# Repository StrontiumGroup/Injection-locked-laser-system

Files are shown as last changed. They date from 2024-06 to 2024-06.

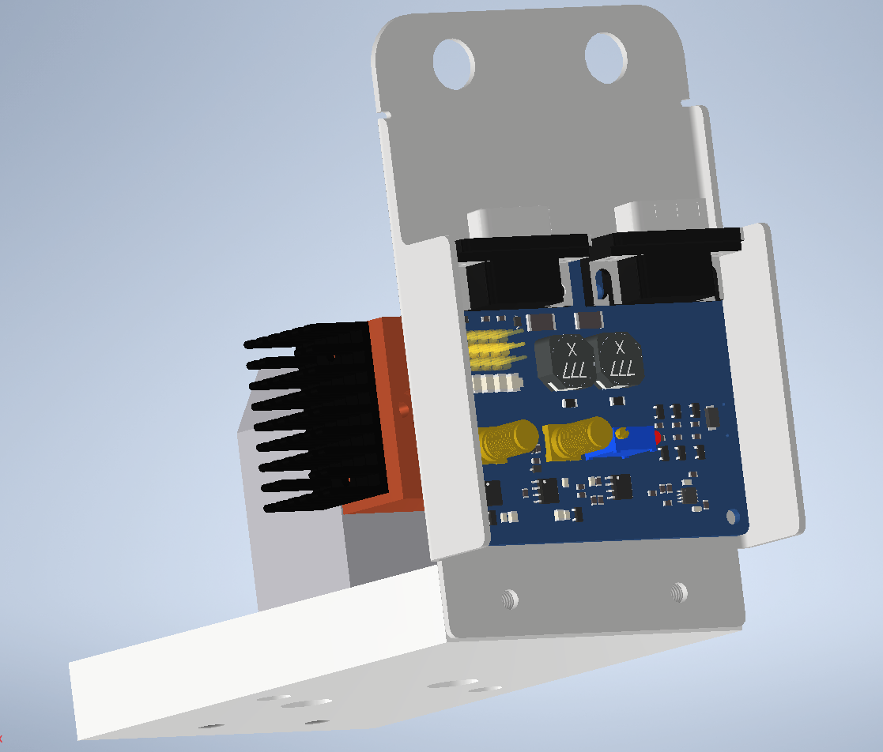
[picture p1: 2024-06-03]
Pictures/Assembly1.png

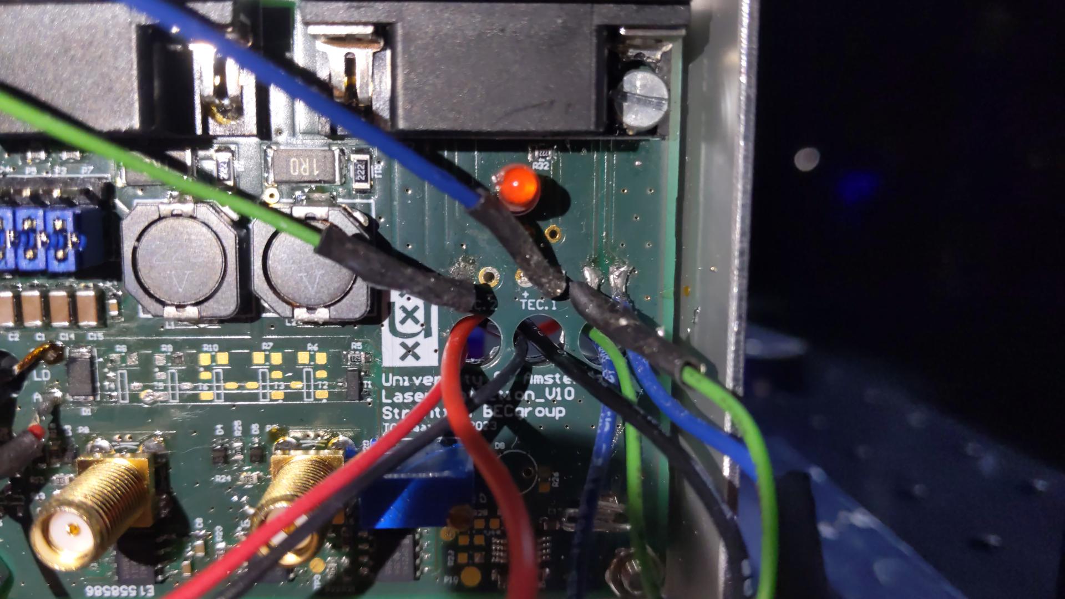
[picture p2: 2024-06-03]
Pictures/SN1/sn1_b.jpeg

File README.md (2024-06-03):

23-0064 Laser diode collimator holder-01
WhatsApp Image 2024-06-03 at 14 32 54 (1)
WhatsApp Image 2024-06-03 at 14 32 54
Assembly1
Assingment


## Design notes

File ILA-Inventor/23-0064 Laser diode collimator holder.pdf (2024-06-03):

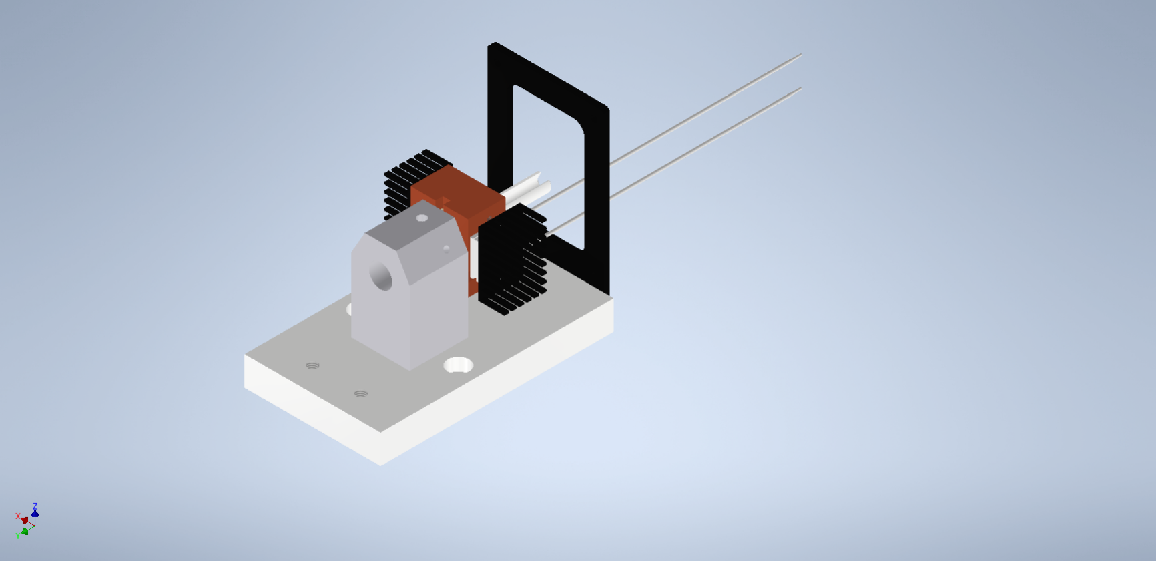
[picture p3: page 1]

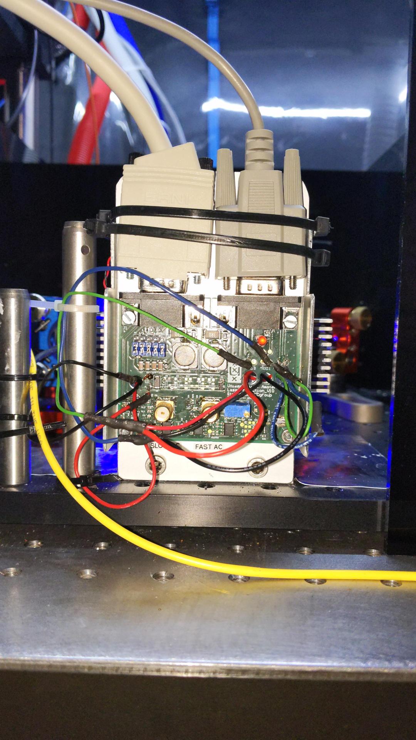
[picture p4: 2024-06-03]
Pictures/SN1/sn1_a.jpeg

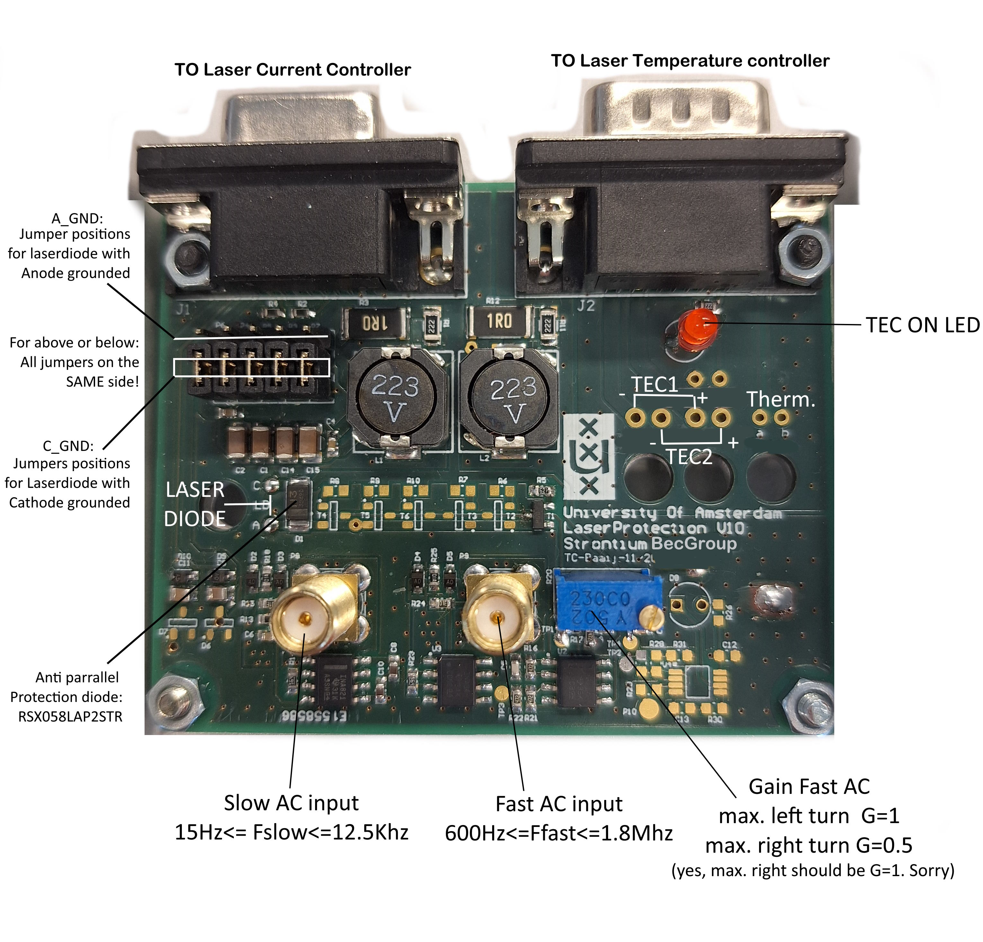
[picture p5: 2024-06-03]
Pictures/SN2/Assingment.jpg

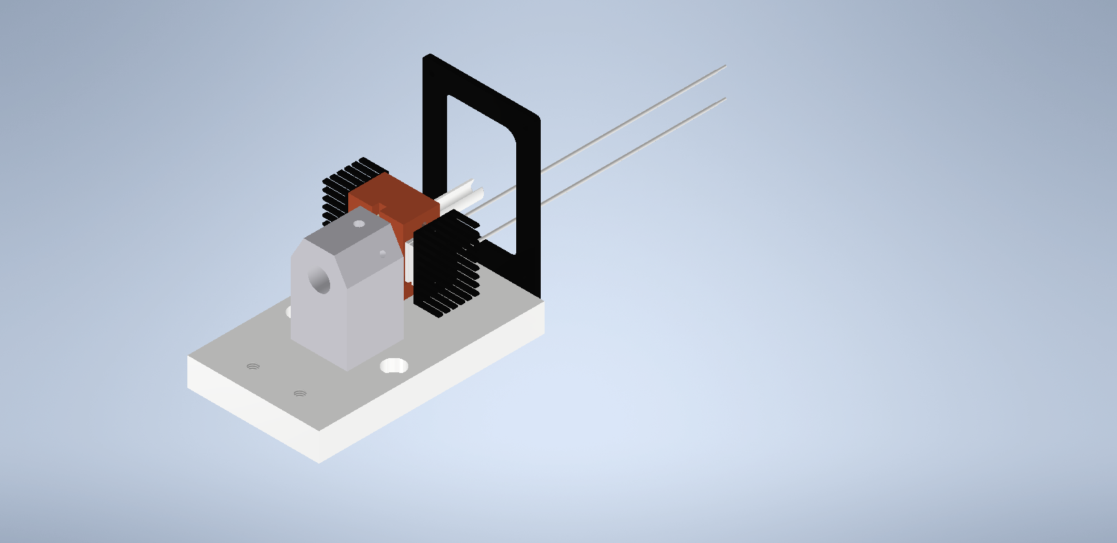
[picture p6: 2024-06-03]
ILA-Inventor/23-0064 Laser diode collimator holder.png

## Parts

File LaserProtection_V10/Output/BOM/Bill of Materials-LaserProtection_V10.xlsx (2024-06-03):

Designator | Quantity | Partname | Description | Footprint | Supplier 1 | Supplier Part Number 1
C1, C2, C14, C15 | 4 | C3216X5R1A107M160AC | MLCC 100 µF, 10 V, 1206 [3216 Metric], ± 20%, X5R | cap1206MD | Farnell | 2211193
C3, C4 | 2 | Cap0603MD_100n_X7R_50V_10% |  | cap0603MD | Farnell | 2581046
C5 | 1 | Cap0603MD_5p_NP0_50V_5% |  | cap0603MD | Farnell | 1759046
C6 | 1 | Cap0603MD_1n5_NP0_50V_5% |  | cap0603MD | Farnell
C7, C8, C10, C12 | 4 | Cap0603MD_1u_X5R_50V_10% |  | cap0603MD | Farnell | 3013383
C9, C11 | 2 | Cap0805MD_10u_X5R_25V_10% |  | cap0805MD | Farnell | 1735530
C13 | 1 | Cap0603MD_10u_X7R_10V_10% |  | cap0603MD | Mouser | 81-GRM188Z71A106KA3D
D1 | 1 | RSX058LAP2STR | Schottky Diode, 3A, 200V, Vf=0.84 (3A/35C), Ir=5-100nA | SODFL470X110-2N | Mouser | 755-RSX058LAP2STR
D2, D3, D4, D5, D9, D10 | 6 | PESD12VL1BA,115 | TVS Diode, Bidirectional, 12V, SOD-323, 2 Pins | SOD-323-2-NoPol | Farnell | 8737363
D6, D7 | 2 | PLVA665A,215 | Zener 6v5, 250mW, 3%, SOT-23 | SOT95P230X110-3N | Mouser | 771-PLVA665A215
D8, D11 | 2 | LED_3mm | Generic 3mm LED Footprint | LED_3mm | Mouser | 710-151031SS04000
Graph1 | 1 | UvA_Logo_Small_horizontal | University of Amsterdam Logo | UVA_LOGO_SMALL_HOR | <no part>
J1 | 1 | 182-009-213R531 | NorComp, D-SUB, 9 pins, Female, right angled PCB | 182-009-213Ryy1 | Farnell | 2294288
J2 | 1 | 182-009-113R531 | NorComp, D-SUB, 9 pins, Male, right angled PCB | 182-009-113Ryy1 | Farnell | 2294285
L1, L2 | 2 | MSS1048T-223MLC | Power Inductor, SMD, 22 µH, 3.58 A, Shielded, 2.36 A | INDP102100X51N | Farnell | 2288292
MH1, MH2 | 2 | MountingHole M3 NP | MountingHole NP for M3, drill 3.2mm, keepout dia 6.5 | MountHole M3 NP keepout 6_5mm | Farnell
MH3, MH4, MH5, MH6 | 4 | MountingHole 5.0mm No keepout | MountingHole 5mm No keepout | MountHole 5mm NP No keepout | Farnell
P1, P2 | 2 | SolderPad_PT_c1.5h0.7mm | SolderPad_PT_c1.5h0.7mm | Pad_PT_c15h07mm | Farnell
P3, P4, P5, P6, P7 | 5 | Header254-1x3 | Header 2.54p 1x3 | Header254-1x3 | Farnell | 1022248
P8, P9 | 2 | PCB.114SMAFSTJ.A | SMA Coaxial, 17.7mm, 50 Ohm, Straight Jack, Through Hole | PCB114SMAFSTJ | Mouser | 960-PCB.114SMAFSTJ.A
P10 | 1 | SolderPad_SMD_c2.0mm | SolderPad_SMD_c2.0mm | Pad_SMD_c20mm | Farnell
P11, P12, P13, P14 | 4 | SolderPad_PT_c1.6h0.8mm | SolderPad_PT_c1.6h0.8mm | Pad_PT_c16h08mm | Farnell
P15, P16, P17, P18 | 4 | SolderPad_PT_c2.0h1.0mm | SolderPad_PT_c2.0h1.0mm | Pad_PT_c20h10mm | Farnell
R1, R11 | 2 | Res1206MD_2K2_1% |  | res1206MD | Farnell
R2, R4, R13 | 3 | Res0603MD_10K_1% |  | res0603MD | Farnell | 2446547
R3, R12 | 2 | RC2512JK-7W4R7L | SMD Chip Resistor, 4.7 ohm, ± 5%, 2 W, 2512 | RES2512MD | Farnell | 1376977
R5, R6, R7, R8, R9, R10 | 6 | Res0603MD_10R_1% |  | res0603MD | Farnell | 2447233
R14, R23 | 2 | Res0603MD_560K_1% |  | res0603MD | Farnell | 9331379
R15, R24 | 2 | Res0603MD_1M_1% |  | res0603MD | Farnell | 2447285
R16, R17, R19, R21, R22, R26 | 6 | Res0603MD_4K7_1% |  | res0603MD | Farnell | 2447385
R18, R25 | 2 | Res0603MD_100R_1% |  | res0603MD | Farnell | 1576263
R20 | 1 | 3296Y-1-502LF | 5K, 25 Turn, Top adjust thruhole trimpot Bourns 100pm | Bourns 3296Y | Farnell | 9353631
R27, R28, R29, R31 | 4 | Res0603MD_Generic |  | res0603MD | Farnell
R30 | 1 | Res0603MD_270R_1% |  | res0603MD | Farnell | 9330917
R32 | 1 | Res0805HD_Generic |  | res0805HD | Farnell
T1, T2, T3 | 3 | MMBF5103 | JFET N Channel, VdgMax=40V, Idss=10 to 40mA, VgsOff=-1.2 to-2.7 V, SOT-23-3 | SOT95P230X110-3N | Farnell | 2454011
T4, T5, T6 | 3 | MMBF4093 | JFET N Channel, VdgMax=40V, Idss=8 to ?mA, VgsOff=-1 to -5V, SOT-23-3 | SOT95P230X110-3N | Farnell | 2992317
U1, U3 | 2 | INA821ID | InAmp, noise=7 nV/√Hz, Ofs=10 µV, Bw=4.7MHz, ± 2.3V to ± 18V, 4.6V to 36V, ±40 input protection | SOIC127P600X175-8N | Mouser | 595-INA821IDR
U2 | 1 | OPA2145IDR | Dual OpAmp, 5.5MHz, Noise=7nV, Ibias=2pA, ±2.3 to ±18v, UnityGain stable, Sot23-5 | SOIC127P600X175-8N | Mouser | 595-OPA2145IDR
U4 | 1 | MC33161DMR2G | 2-40V Window Comparator, internal ref (2.54/1.27V), open collector out | TSOP65P490X110-8N | farnell | 2774746

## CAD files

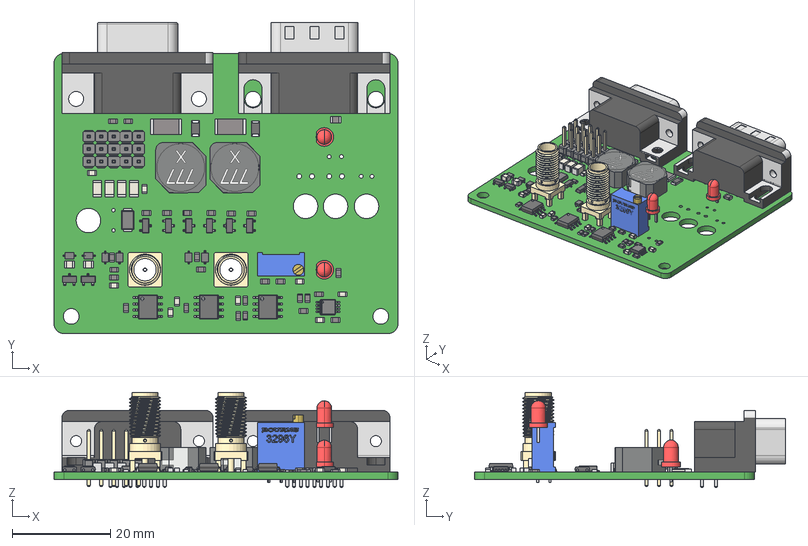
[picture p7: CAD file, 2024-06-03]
Laser_Pretection_Board_CAD/LaserProtection_V10.step
70.0 x 63.3 x 19.4 mm
Extruded x 132
CircuitWorks-LED DIP 3MM x 2
lead x 2
Leader x 8
User Library-SOIC-8-1 x 3
User Library-SOT95P240X100-3-ONSEMI_SOT-23 x 8
User Library-3296Y
User Library-CR3216-1206 x 2
CONSMA008-G x 2
Header254 1x3 M20-9990345 x 5
Coilcraft-MSS1048T x 2
SOD323_DIO x 6

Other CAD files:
ILA-Inventor/23-0064 Laser diode collimator holder.iam
ILA-Inventor/23-0064 PCB plate.ipt
ILA-Inventor/23-0064 Adjustment tool.ipt
ILA-Inventor/23-0064 Base plate.ipt
ILA-Inventor/23-0064 Cooling block.ipt
ILA-Inventor/23-0064 Diode holder.ipt
ILA-Inventor/K+S 20C-A4.5-07.ipt
ILA-Inventor/TECF1S.ipt
ILA-Inventor/ick_bga_33x33x14.ipt
Laser_Pretection_Board_CAD/CONSMA008-G--3DModel-STEP-56544.iam
Laser_Pretection_Board_CAD/CONSMA008-G.ipt
Laser_Pretection_Board_CAD/Enclosure-Cap.ipt
Laser_Pretection_Board_CAD/Enclosure.ipt
Laser_Pretection_Board_CAD/Enclosure_Base.ipt
Laser_Pretection_Board_CAD/M20-9990345--3DModel-STEP-56544.ipt
Laser_Pretection_Board_CAD/Nut.ipt
Laser_Pretection_Board_CAD/Washer.ipt

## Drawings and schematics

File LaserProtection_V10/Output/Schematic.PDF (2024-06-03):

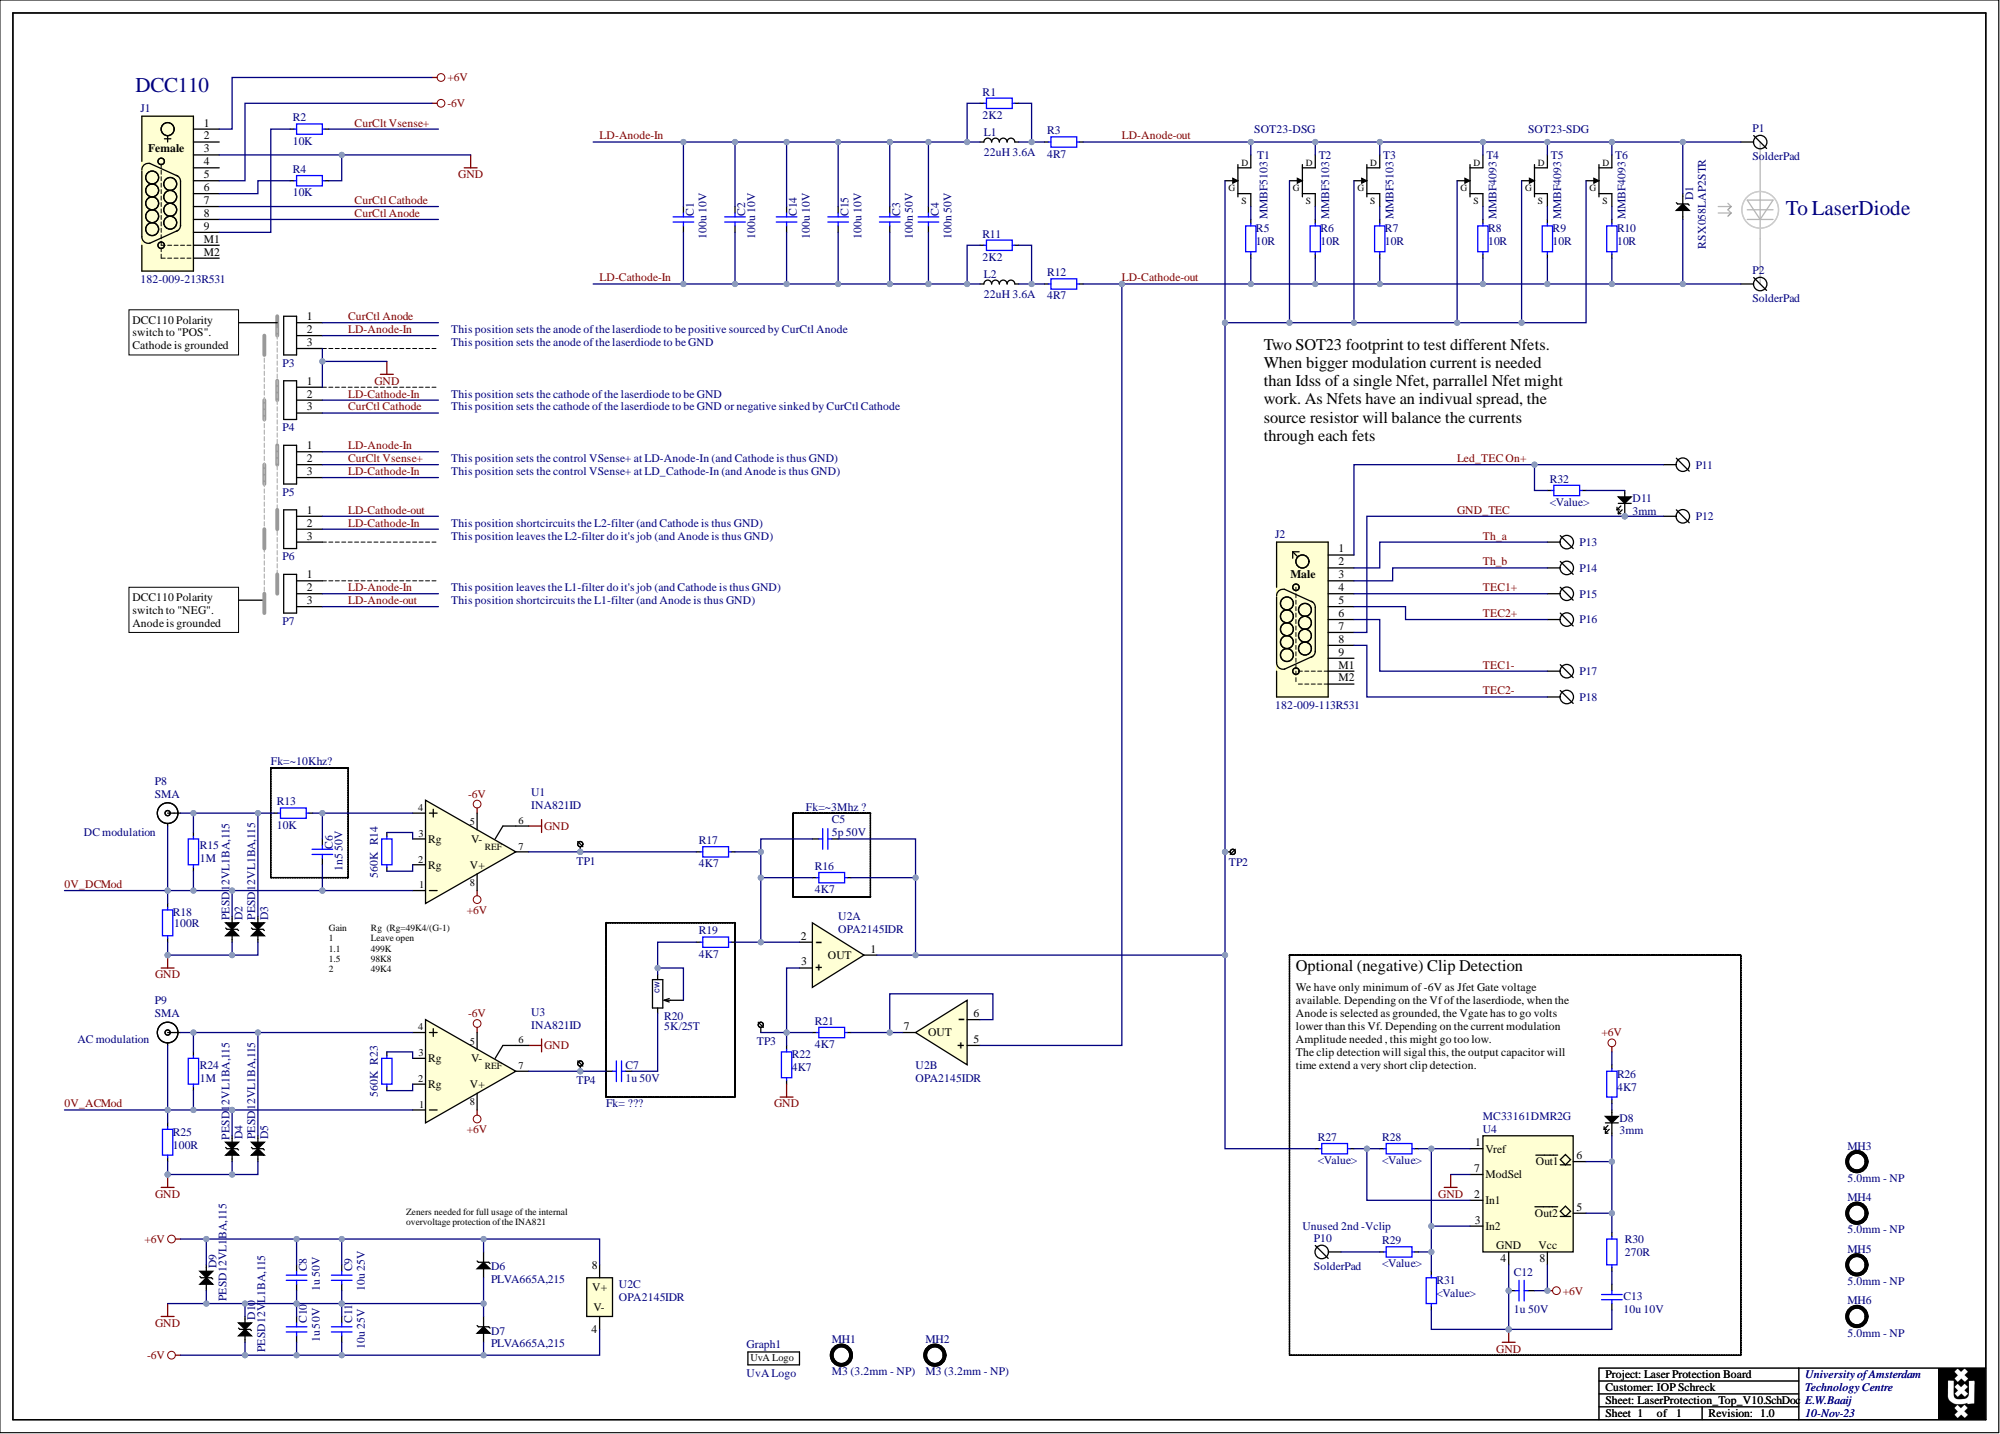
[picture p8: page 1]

6 | CurCtl Cathode
8 | CurCtl Anode

This position sets the anode of the laserdiode to be positive sourced by CurCtl Anode
This position sets the anode of the laserdiode to be GND

Two SOT23 footprint to test different Nfets.
When bigger modulation current is needed
than Idss of a single Nfet, parrallel Nfet might
work. As Nfets have an indivual spread, the
source resistor will balance the currents
through each fets

This position sets the cathode of the laserdiode to be GND
This position sets the cathode of the laserdiode to be GND or negative sinked by CurCtl Cathode

This position sets the control VSense+ at LD-Anode-In (and Cathode is thus GND)
This position sets the control VSense+ at LD_Cathode-In (and Anode is thus GND)

This position shortcircuits the L2-filter (and Cathode is thus GND)
This position leaves the L2-filter do it's job (and Anode is thus GND)

This position leaves the L1-filter do it's job (and Cathode is thus GND)
This position shortcircuits the L1-filter (and Anode is thus GND)

Optional (negative) Clip Detection

We have only minimum of -6V as Jfet Gate voltage
available. Depending on the Vf of the laserdiode, when the
Anode is selected as grounded, the Vgate has to go volts
lower than this Vf. Depending on the current modulation
Amplitude needed , this might go too low.
The clip detection will sigal this, the output capacitor will
time extend a very short clip detection.

Zeners needed for full usage of the internal
overvoltage protection of the INA821

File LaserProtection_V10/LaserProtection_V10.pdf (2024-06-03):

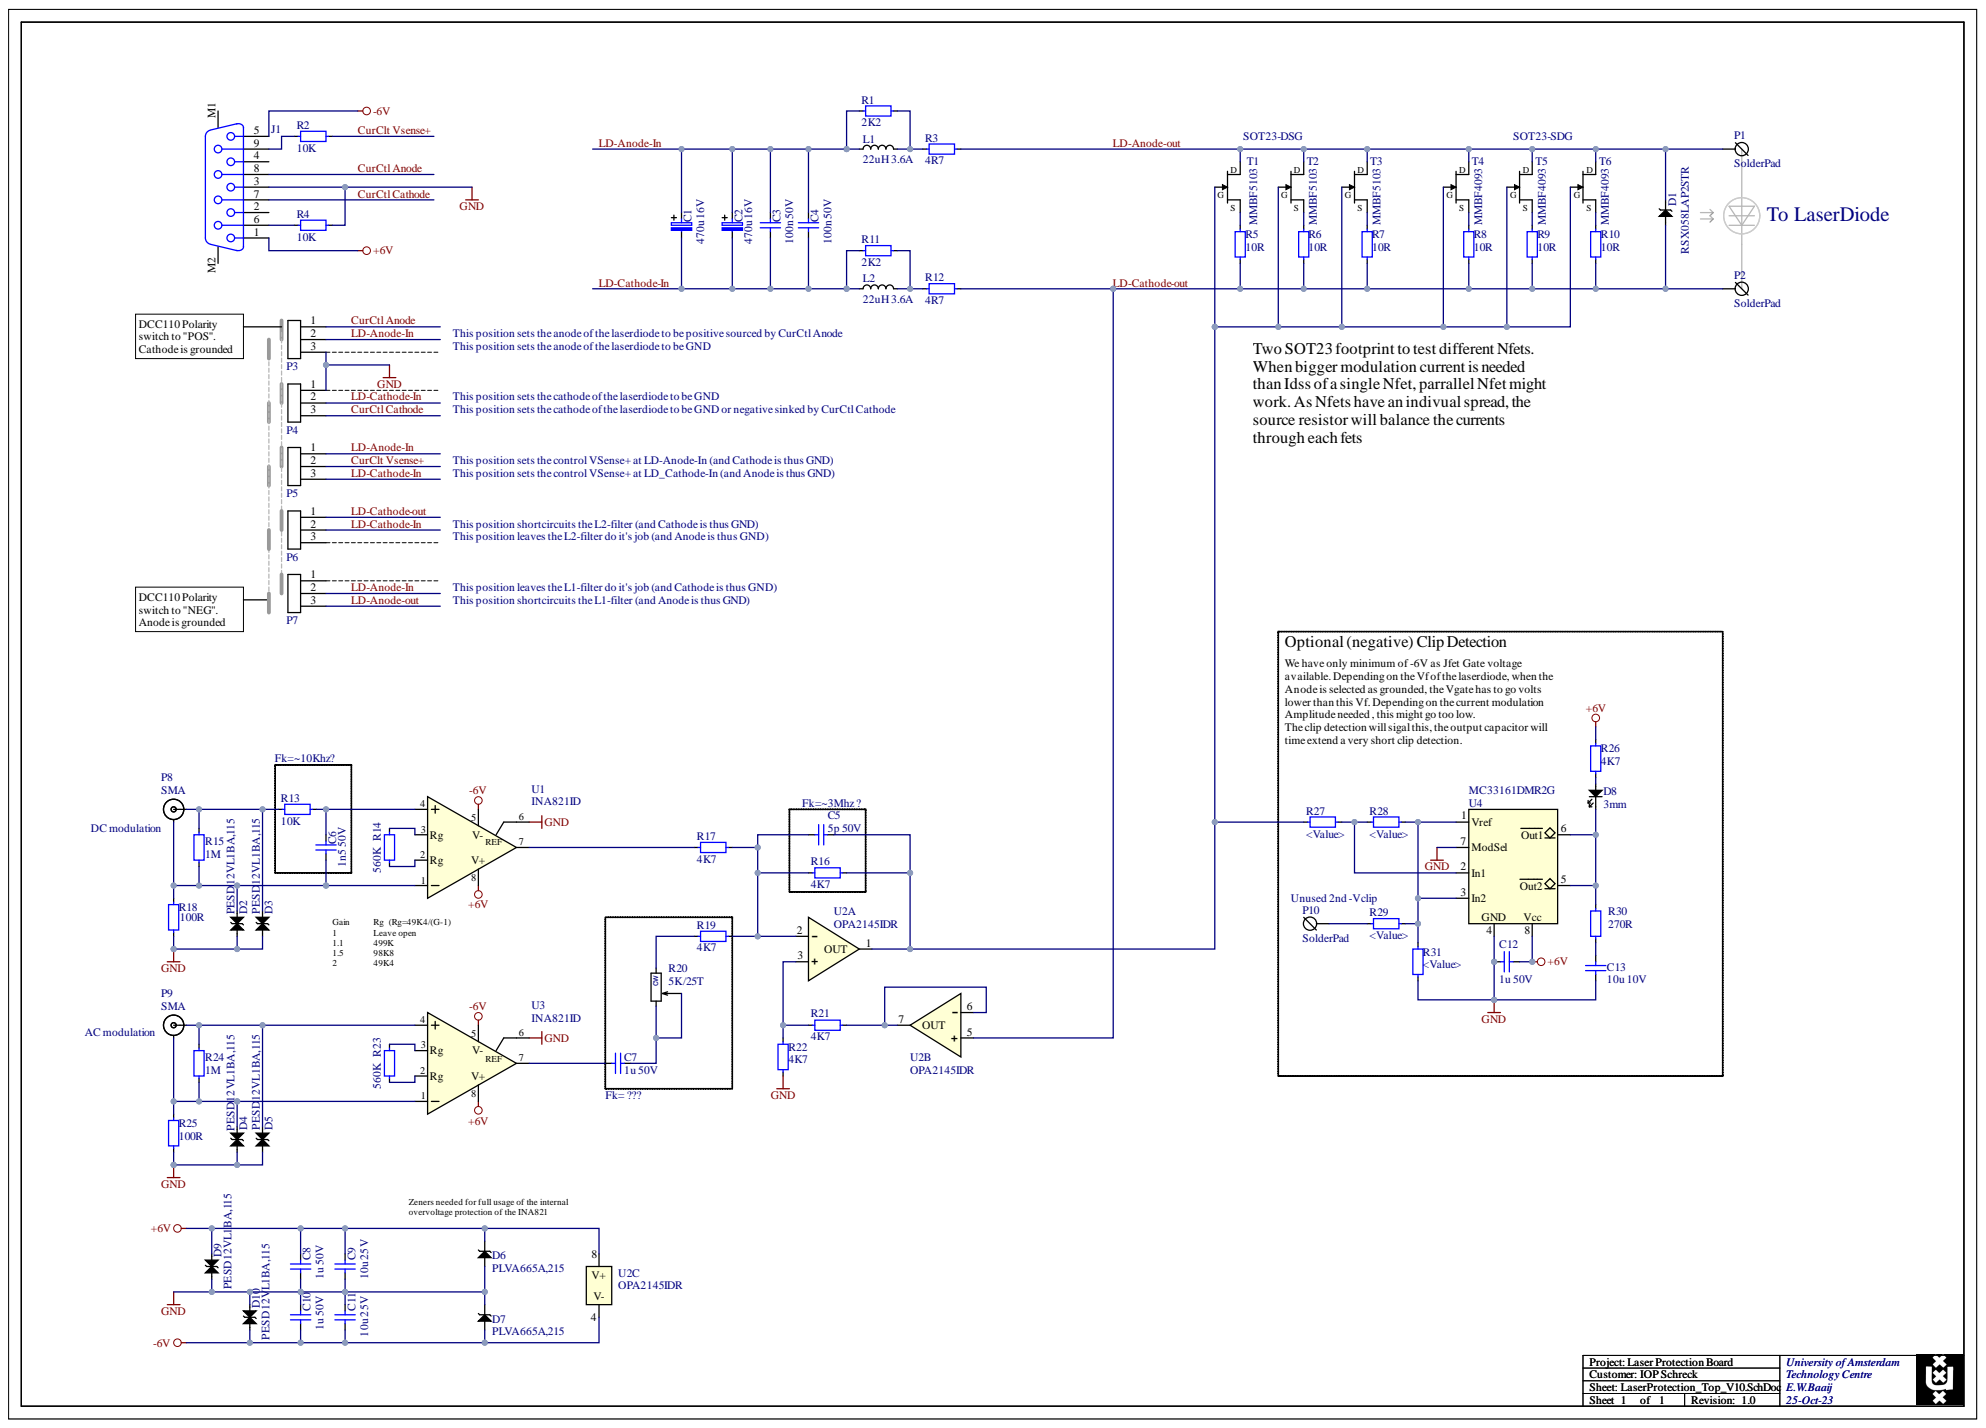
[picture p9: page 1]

This position setsthe anode ofthe laserdiode to be positive sourced by CurCtlAnode
This position setsthe anode ofthe laserdiode to beGND

Two SOT23 footprint to test different Nfets.
When bigger modulation current is needed
than Idss of a single Nfet, parrallel Nfetmight
work. As Nfets have an indivualspread, the
source resistor will balance the currents
through each fets

This position setsthe cathode ofthe laserdiode to beGND
This position setsthe cathode ofthe laserdiode to beGND or negative sinked by CurCtlCathode

This position setsthe controlVSense+ at LD-Anode-In (and Cathode isthus GND)
This position setsthe controlVSense+ at LD_Cathode-In (and Anode isthus GND)

This position shortcircuitstheL2-filter (and Cathode isthus GND)
This position leavestheL2-filter do it'sjob (and Anode isthus GND)

This position leavestheL1-filter do it'sjob (and Cathode isthus GND)
This position shortcircuitstheL1-filter (and Anode isthus GND)

Optional(negative) Clip Detection

We have only minimum of -6V as Jfet Gate voltage
available. Depending on theVf ofthe laserdiode, when the
Anode isselected as grounded, theVgate hasto go volts
lower than this Vf. Depending on the current modulation
Amplitude needed , this might go too low.
The clip detection willsigal this, the output capacitor will
time extend a very short clip detection.

<Value> | | ModSel 7

- 2 | U2A OPA2145IDR | | R29 | In2 3

Zeners needed for full usage of the internal
overvoltage protection of the INA821

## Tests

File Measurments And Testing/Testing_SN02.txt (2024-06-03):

v-No Shorts ±6V
v-Apply ±6V / 100mA -> PwerSup ON -> meas. ±9mA
>- 50Ohm term on inputs
v- U1 out 0V
v- U3 out 0V

>-Apply 100Hz/500mVtt @ slow AC in
v- scope measure rising freq. to signal=356mV (=-3dB); 12.5Khz (high cut-off)
v- measure same signal on Tp2 (U2A-out)
v- scope measure decreasing freq. to signal=356mV (=-3db); 15Hz (lo ccut-off)

>-turn potmeter far left (is max gain; trimpot wrong wired)
>-Apply 100Khz/500mVtt @ fast AC in
v-scope measure rising freq. to signal=356mV (=-3dB); 1.8Mhz (high cut-off)
v-scope measure decreasing freq. to signal=356mV (=-3db); 600Hz (lo ccut-off)

>-Apply pos. curren 3V / 50mA
>- connect yellow led
v- At both input 0V measure 1.28V over Source res. 620R -> (=2mA)

>-Apply 2Vtt at slow input
v-measure Vtt over Rsource; 1.52V

>-Apply 2Vtt at Fast input
v-measure Vtt over Rsource; ~1.52V
